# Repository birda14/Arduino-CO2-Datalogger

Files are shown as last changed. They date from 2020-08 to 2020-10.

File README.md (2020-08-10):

# Arduino-CO<sub>2</sub> efflux Datalogger
An arduino sketch to log measurements from multiple environmental sensors to an SD card. For use in a soil CO<sub>2</sub> efflux chamber. 

## Construction 
Required Components:
Component | Quantity | Store Link
---|---|---
 Arduino UNO | 1 | https://amzn.to/2EKhSgj
 Adafruit Datalogging Shield | 1 | https://bit.ly/3kf1W69
 CR1220 Coin Cell Battery | 1 | https://bit.ly/2DmNJ6x
 SD Card | 1 | https://amzn.to/3ibLDoG
 Headers | 1 | https://amzn.to/3gwQX5M
 Perma-proto Half Sized Breadboard | 1 | https://bit.ly/3kfBTf6
 Adafruit BME680 (Temperature, Humidity, Pressure, VOC) | 1 | https://bit.ly/39WR7AS
 DS18B20 Waterproof Temperature Sensor | 1 | https://amzn.to/3keA4Po
 T6613 CO<sub>2</sub> Analyzer | 1 | https://bit.ly/2DdPLpG
 Piezo Buzzer | 1 | https://amzn.to/3gAVuEg
 4.7K Resistor | 1 | https://amzn.to/39Ylmau
 Cable gland | 2 | https://bit.ly/31ouS2S
 Case | 1 | https://amzn.to/39YkZwC
 50cm of 3' PVC pipe | 1 | Local Retail
 3' PVC cap | 1 | Local Retail
 Velcro Tape | 1 | https://amzn.to/2EKnJ5h
 18 AWG Wire | 1 | https://amzn.to/3ki2Q1w
 22 AWG Wire | 1 | https://amzn.to/2XtdvN6
 Battery Box | 1 | https://bit.ly/3fvNumH
 Power Connector | 1 | https://amzn.to/3gCqHHm
 AA Batteries 8 pack | 1 | https://amzn.to/2PoqyLD
 
 ### Assemble Arduino
 1. Solder header pins onto the datalogger shield.
 2. Connect the datalogger shield to the Arduino Uno. 
 3. Install the real time clock CR1220 coin cell battery into the datalogger shield.

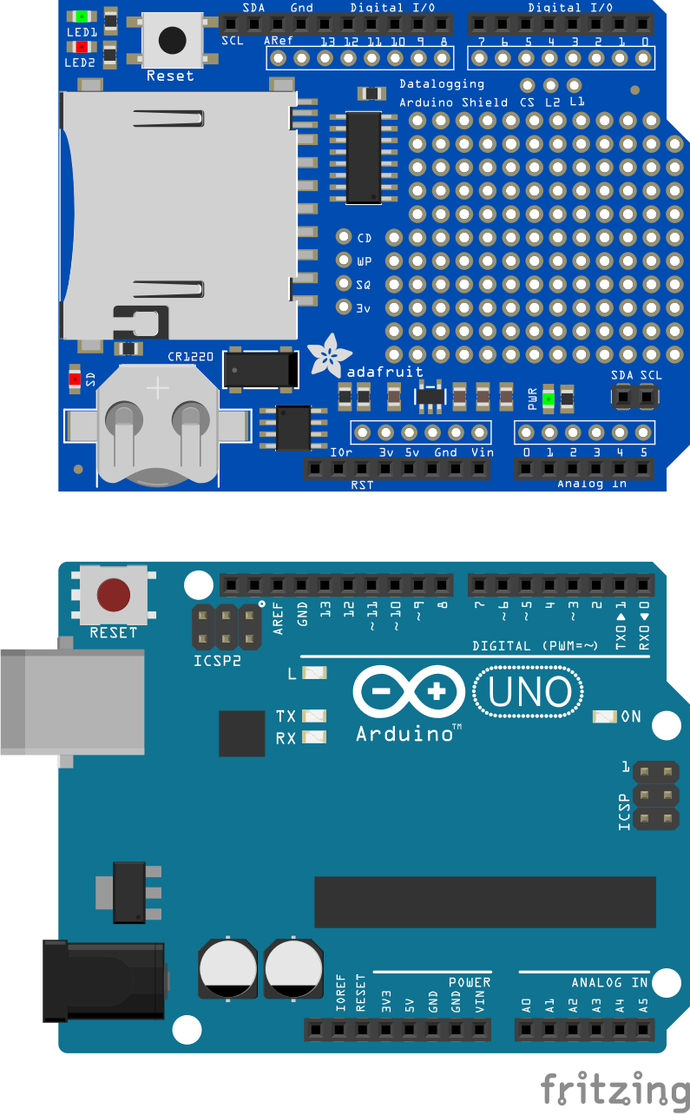
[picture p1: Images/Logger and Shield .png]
Shield and Uno
  

 ### Assemble Sensor Board
 1. Solder header pins to all connections on the BME680
 2. Solder individual header pins to only pins 1, 3, 10, and 11 of the T6613 CO<sub>2</sub> sensor (see pinout below).

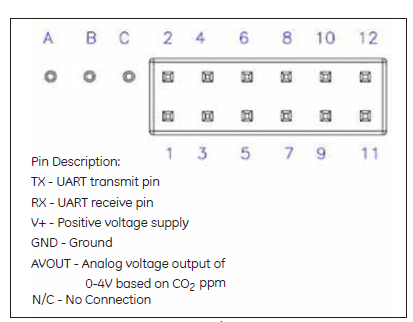
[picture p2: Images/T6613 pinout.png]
T6113 pinout
 

 3. Connect all componets to the board as per the diagram and table below. 

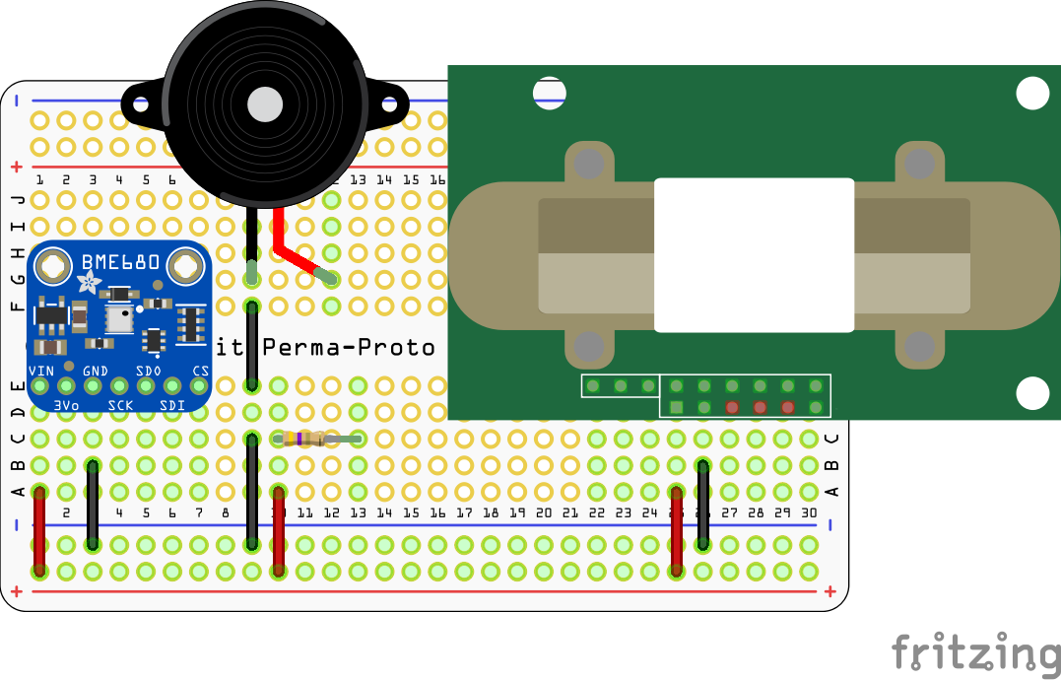
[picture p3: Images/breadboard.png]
Sensor board
  

 Component | Pin | Board Position
 ---|---|---
 BME680 | VIN | E1
 BME680 | 3Vo | E2
 BME680 | GND | E3
 BME680 | SCK | E4
 BME680 | SDO | E5
 BME680 | SDI | E6
 BME680 | CS | E7
 Buzzer | - | I9
 Buzzer | + | I12
 T6613 | 1 | D25
 T6613 | 3 | D26
 T6613 | 10 | E29
 T6613 | 11|  D30

 Component | Board Position 1 | Board Position 2
 ---|---|---
 Black Wire 1 | Ground 3 | B3 
 Black Wire 2 | Ground 9 | C9
 Black Wire 3 | E9 | F9
 Black Wire 4 | Ground 26 | B26
 Red Wire 1 | Positive 1 | A1
 Red Wire 2 | Positive 10 | A10
 Red Wire 3 | Positive 25 | A25
 4.7K Resistor | C10 | C13

 ### Assemble Chamber
 1. Cut a 50cm length of 3 inch diameter PVC pipe.
 2. Place a PVC cap on one end of the tube.
 3. Measure one inch from the bottom of the cap and mark it. Drill a hole with a 1/2" drill bit. 
 4. Measure the center of the waterproof case and mark it. Drill a hole with a 1/2" drill bit.
 5. Install 2 cable glands into the newly-drilled holes. 
 6. Cut the barrel connector of of the battery box and strip both wires.
 7. Run the battery cable through the cable gland into the waterproof case and connect it to the power connector with a screwdriver
 8. Attach the waterproof case and the battery box to the top of the PVC piping using velcro tape.  

 ### Wiring 
 1. Cut 8 coloured wires 40cm in length. 
 2. Run the wires through both cable glands, from the inside of the chamber to the inside of the waterproof case. 
 3. Run the waterproof temperature sensor wires through the chamber cable gland.
 4. Solder the connections between the Arduino and sensor board according to the following table and diagram:

 Component | Arduino Position | Board Position 
 ---|---|---
 Orange Wire | Snslog In 4 | A6
 Purple Wire | Analog In 5 | A4
 Red Wire | 5.0V | Positive 30
 Black Wire | GND | Negative 30
 Grey Wire | Digital I/O 6 | A29
 White Wire 1 | Digital I/O 7 | A30 
 White wire 2 | Digital I/O 8 | A14
 Brown Wire 9 | Digitcal I/O 9 | F12
 DS18B20 Red Wire |  | B10
 DS18B20 Black Wire | | D9
 DS18B20 Yellow Wire | | D14

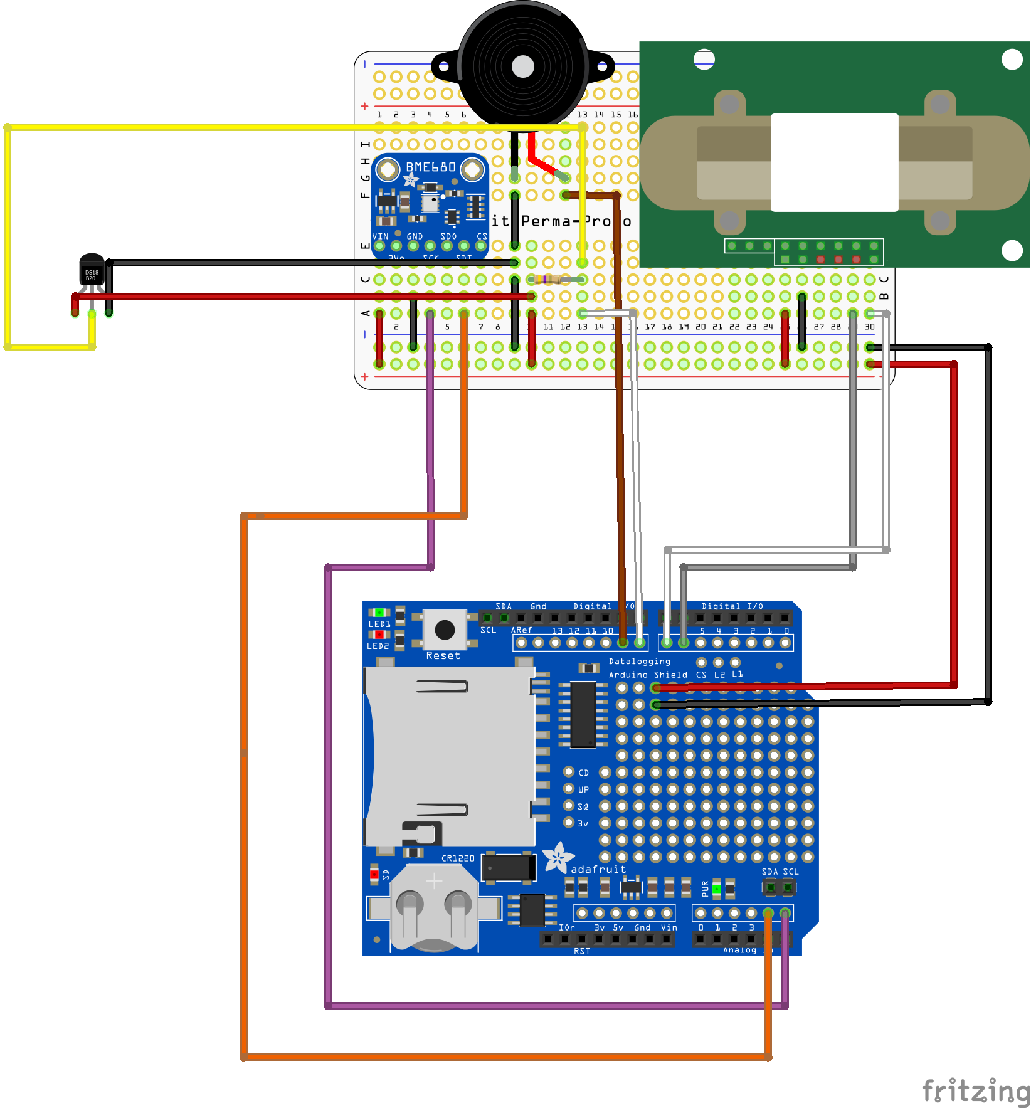
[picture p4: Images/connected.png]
Connected
 
## Programming The Arduino 
 Download and install Arduino IDE for your platform:

https://www.arduino.cc/en/Main/Software

### Required Libraries  
1. In the Arduino IDE click Tools -> Manage Libraries.
2. Search for and install the following libraries:

```C++
#include <SD.h> //Library for SD card Logger
#include <Wire.h> //Library for I2C Interface
#include <SPI.h> //Library for SPI interface
#include <Adafruit_Sensor.h> //Common Library for Adafruit Unified Sensors 
#include "Adafruit_BME680.h" // Library for Combined Environmental Sensor BME680
#include "SoftwareSerial.h" //Library for Configuring Serial Interface for T6613 CO2 Sensor
#include "RTClib.h" //Library for Real Time Clock RTC_PCF8523
#include <OneWire.h> //Interface for DS18B20 Temperature Sensor
#include <DallasTemperature.h> //Library for DS18B20 Temperature Sensor
```

### Preparing the Real-Time-Clock (RTC)
1. In the Arduino IDE click Files -> Examples -> RTClib -> PCF8523
2. Uncomment line 38 and upload to the Arduino to set the clock based on the PC system time. 

### Preparing the SD Card 
1. Format an SD card in FAT32 using your operating system utility.
2. Insert it into the datalogging shield. 

### Customizing and Uploading the Program
 1. Download datalogger_sketch.ino 
 2. Open sketch in Arduino IDE or the editor of your choice.
 3. Edit line 71 to change the total sampling duration (default is 3 minutes).
 4. Edit line 120 to change the sampling interval (default is 5 seconds). 
 5. Upload datalogger.sketch to your arduino board. 

## Field Operation
1. Set the chamber down on its side near the preinstalled soil collar you wish to measure from. Turn on the device with the power toggle switch on the battery box.  
2. The device will enter a warmup period for 5 minutes.
3. While you wait, unclip the soil moisture sensor and insert it into the soil beside the collar. 
4. At the end of 5 minutes the device will beep for 3 seconds. When this occurs, pick up the device and secure it into the soil collar. 
5. The device will log every 5 seconds for 3 minutes. A red light will blink twice every 5 seconds to indicate logging. 
6. When 3 minutes has elapsed, the device will beep for 5 seconds. The red light will stop blinking to indicate that logging has ended. 
7. Turn off the device using the power switch on the battery box.  

## Data 
The device logs the following 8 variables to an SD card in .csv format: 
- Site/Location/Station
- Date
- Time
- Atmospheric temperature (in Kelvin)
- Soil temperature (in Kelvin)
- Atmospheric humididy (in Percent)
- Atmospheric pressure (in kPa)
- Atmospheric CO<sub>2,</sub> concentration

Station | Date | Time | Air Temp (K) | Soil temp (K) | Humidity (%) | Air press (kPa) | CO<sub>2</sub> (ppm) |
---|---|---|---|---|---|---|---|
Site 1 | 08/05/2020 | 8:51:07 | 298.54 | 298.15 | 67.81 | 100.3 | 380
Site 1 | 08/05/2020	| 8:51:12 |	298.55 | 297.96 | 67.69 | 100.3 | 380
Site 1 | 08/05/2020	| 8:51:17 |	298.56 | 297.9 | 67.51 | 100.3 | 381
Site 1 | 08/05/2020	| 8:51:22 |	298.58 | 297.9 | 67.38 | 100.3 | 381
Site 1 | 08/05/2020	| 8:51:27 |	298.6  | 297.9 | 67.28 | 100.3 | 380

## Reference Photos

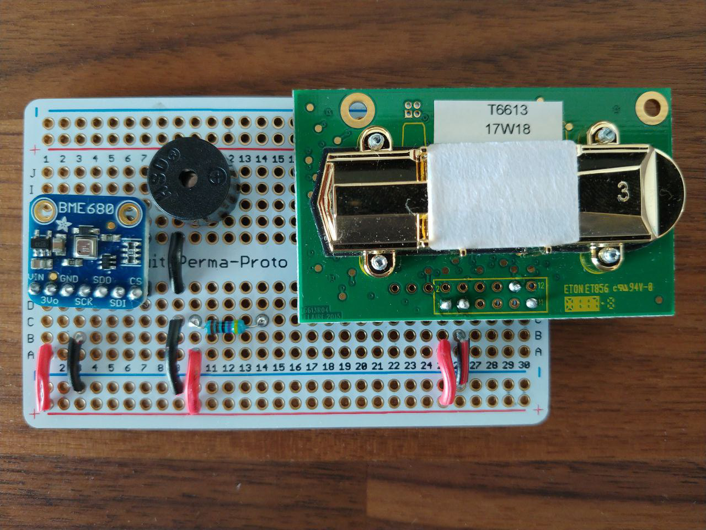
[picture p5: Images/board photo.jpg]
Breadboard

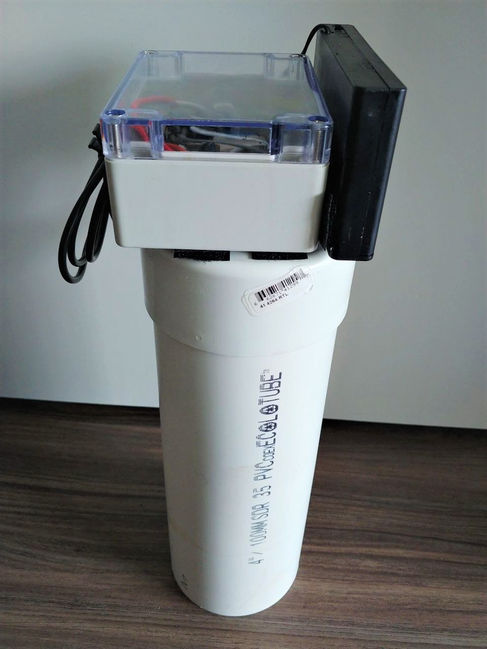
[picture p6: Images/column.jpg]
Column

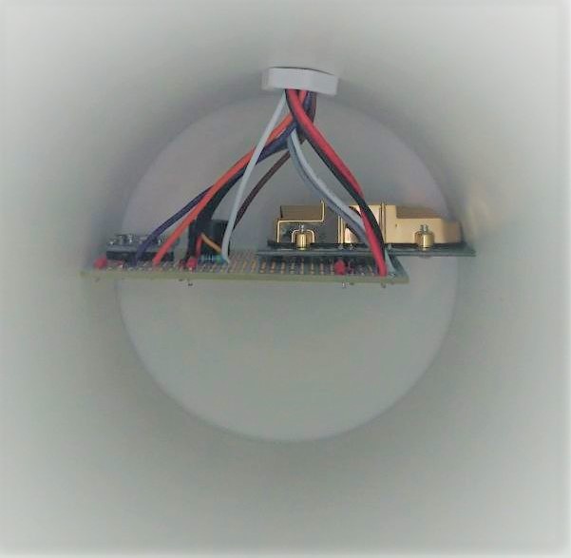
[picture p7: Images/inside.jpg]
Inside

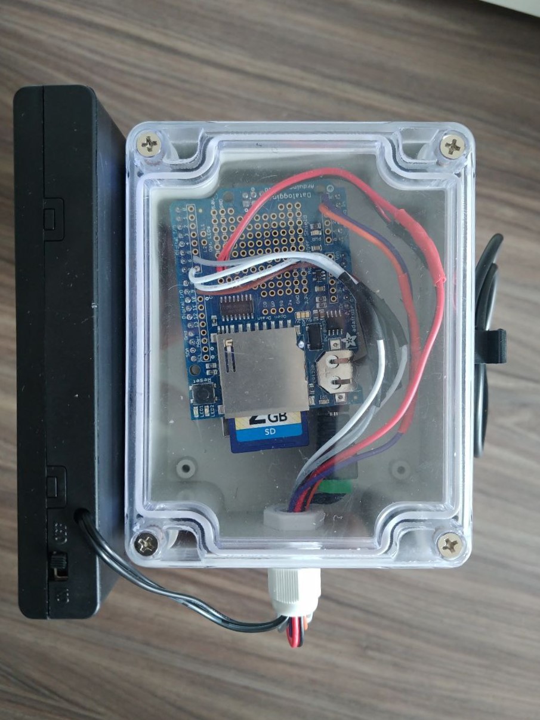
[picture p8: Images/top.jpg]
Top


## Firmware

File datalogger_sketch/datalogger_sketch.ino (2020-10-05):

//Include required libraries
#include <SD.h> //Library for SD card Logger
#include <Wire.h> //Library for I2C Interface
#include <SPI.h> //Library for SPI interface
#include <Adafruit_Sensor.h> //Common Library for Adafruit Unified Sensors 
#include "Adafruit_BME680.h" // Library for Combined Environmental Sensor BME680
#include "SoftwareSerial.h" //Library for Configuring Serial Interface for T66 CO2 Sensor
#include "RTClib.h" //Library for Real Time Clock RTC_PCF8523
#include <OneWire.h> //Interface for DS18B20 Temperature Sensor
#include <DallasTemperature.h> //Library for DS18B20 Temperature Sensor
//----------------------------------------------------------------------

//Set up UART connection for CO2 sensor
SoftwareSerial T66_Serial(6,7); //Sets up a virtual serial port on pin 6 for Rx and pin 7 for Tx
byte readCO2[] = {0xFF, 0XFE,2,2,3}; //T66 read CO2 command: 5 bytes
byte response[] = {0,0,0,0,0}; //create an array to store the response
//---------------------------------------------------------------------

//Set up BME 680 sensor
#define BME_SCK 13
#define BME_MISO 12
#define BME_MOSI 11
#define BME_CS 10
#define ONE_WIRE_BUS 8
#define SEALEVELPRESSURE_HPA (1013.25)
//---------------------------------------------------------------------

// Misc Configuration for Buzzer, BME680, RTC, Dattalogger, DS18B20
const int buzzer = 9; //Set up buzzer on arduino pin 9
Adafruit_BME680 bme; //Set up BME680 I2C
RTC_PCF8523 rtc; //Setup real time clock
const int pinCS = 10; // Set up logging sheild 10 for the SD cs line
OneWire oneWire(ONE_WIRE_BUS);
DallasTemperature sensors(&oneWire);
float Celcius=0;
DateTime sampleinit;
//----------------------------------------------------------------------

void setup()
{
  // put your setup code here, to run once:
  Serial.begin(9600); //Start serial console for debugging
  SD.begin(pinCS); //Start SD card
  bme.begin(); //Start bme sensor
  rtc.begin(); //Start real time clock
 
  // Set up oversampling and filter initialization
  bme.setTemperatureOversampling(BME680_OS_8X);
  bme.setHumidityOversampling(BME680_OS_2X);
  bme.setPressureOversampling(BME680_OS_4X);
  bme.setIIRFilterSize(BME680_FILTER_SIZE_3);
  bme.setGasHeater(320, 150); // 320*C for 150 ms
  sensors.begin();
  sensors.setWaitForConversion(false);
  pinMode(buzzer, OUTPUT); // Set buzzer - pin 9 as an output

  T66_Serial.begin(19200); //Opens the virtual serial port with a baud of 19200

  Serial.println(" Datalogger Start");
  Serial.print("\n");

  delay(300000); //wait 5 minutes for CO2 sensor to warm up before entering the loop
  tone(buzzer, 1000); // Send 1KHz sound signal...
  delay(3000);        // ...for 1 sec
  noTone(buzzer);     // Stop sound...
  delay(1000);        // ...for 1sec  
  sampleinit = rtc.now(); //Store sampling initiated time
}

void loop() {
  if(rtc.now() == (sampleinit+TimeSpan(0,0,3,0))) //Edit to change total sampling duration (day, hour, minute, second)
    { 
      tone(buzzer, 2000); // Send 2KHz sound signal...
      delay(5000);        // ...for 1 sec
      noTone(buzzer);     // Stop sound...
      while(1) { }        //Endless loop, program ends. 
      }
  DateTime now = rtc.now(); // Check time at begining of loop

  if (! bme.performReading()) {
    Serial.println("Failed to perform reading :(");
    return;
  }
  
  File dataFile = SD.open("log.csv", FILE_WRITE); //opens or creates file

  sensors.requestTemperatures(); 
  Celcius=sensors.getTempCByIndex(0);
  sendRequest(readCO2);   //Sends request to CO2 meter
  unsigned long valCO2 = getValue(response);// Request from sensor 5 bytes of data

if (dataFile)
  {
    dataFile.print("Coboconk"); //Edit to change site information 
    dataFile.print(",");
    dataFile.print(now.year(), DEC);
    dataFile.print("/");
    dataFile.print(now.month(), DEC);
    dataFile.print("/");
    dataFile.print(now.day(), DEC);
    dataFile.print(",");
    dataFile.print(now.hour(), DEC);
    dataFile.print(":");
    dataFile.print(now.minute(), DEC);
    dataFile.print(":");
    dataFile.print(now.second(), DEC);
    dataFile.print(",");
    dataFile.print(bme.temperature + 273.15);     //Temperature in Kelvin
    dataFile.print(",");
    dataFile.print(Celcius + 273.15);       //Temperature in Kelvin
    dataFile.print(",");
    dataFile.print(bme.humidity);           //Humidity in %
    dataFile.print(",");
    dataFile.print(bme.pressure / 1000);    //Pressure in kPa
    dataFile.print(",");
    dataFile.print(valCO2);                 //Concentration in ppm
    dataFile.println();
    dataFile.close();

    while(rtc.now() != (now+TimeSpan(0,0,0,5))); //Edit to change total sampling interval (day, hour, minute, second)
    
  }
  else
  {
    Serial.print(dataFile);
  }
}

void sendRequest(byte packet[])
{
 while(!T66_Serial.available()) //keep sending request until we start to get a response
 {
 T66_Serial.write(readCO2,5);// Write to sensor 5 byte command
 delay(50);
 delay(1000);
 }
 int timeout=0; //set a timeoute counter
 while(T66_Serial.available() < 5 ) //Wait to get a 7 byte response
 {
 timeout++;
 if(timeout > 10) //if it takes to long there was probably an error
 Serial.print("Timeout");
 {
 while(T66_Serial.available()) //flush whatever we have
 T66_Serial.read();

 break; //exit and try again
 }
 delay(50);
 }
  for (int i=0; i < 5; i++) response[i] = T66_Serial.read();
}

unsigned long getValue(byte packet[])
{
 int high = packet[3]; //high byte for value is 4th byte in packet in the packet
 int low = packet[4]; //low byte for value is 5th byte in the packet
 unsigned long val = high*256 + low; //Combine high byte and low byte with this formula to get value
 return val;
 
}

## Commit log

2020-08-05 added diagrams to WD, updated readme
    [Decent sketchfzz.fzz]
2020-08-06 add image to readme
    [Decent sketchfzz.fzz]
2020-08-06 updated readme sensor board instructions
